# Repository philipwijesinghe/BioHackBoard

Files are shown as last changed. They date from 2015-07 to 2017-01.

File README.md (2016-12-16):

# BioHackBoard

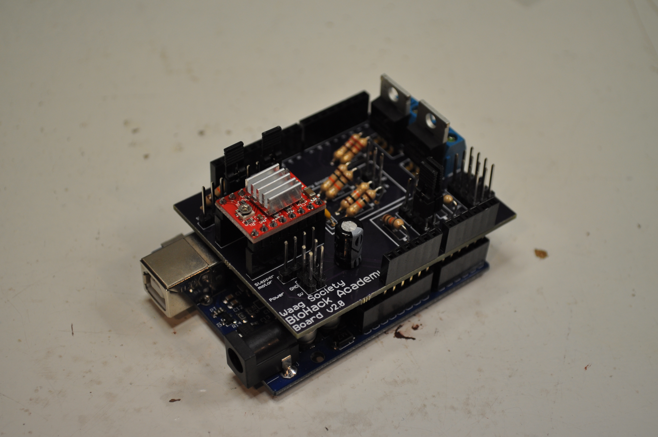
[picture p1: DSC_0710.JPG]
BioHack Board V2.0

The BioHackBaord is an Arduino shield that aims to eliminate the need for any soldering or breadboard for the assembly of BHA devices. 

The shield is able to drive a steppermotor, read a rotary encoders, 2 thermistors, control 2 MOSFETs and connect up to 3 I2C devices, such as an LCD screen.

## Releases

The current version (v2.1) of the board has been designed on the Circuits.io platform. The schematics, PCB design and Gerber files can be found in that [BioHackBoard V2.1 repo](https://circuits.io/circuits/2997842-biohack-board)

The BoM file in this repo lists the parts needed to finish this v2.1 board.

The first version of the board and a kit with additional components was sold by [BioTronics](http://biotronics.nl/products/biohackacademy-prototyping-kit). The source files of this board can be found in this BioHackBoard repository.

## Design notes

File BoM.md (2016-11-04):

## Bill of Materials

These are the parts that need to be soldered on top of a [BioHack Board V2.0](https://circuits.io/circuits/2997842-biohack-board)

### Components 

|No|Amount|Description|Supplier NL|Cost|
| ------------: | ------------: | :------------ | :------------ | ------------: |
|1|2|Screw Terminal|[iPrototype](https://iprototype.nl/products/components/overige/terminal-block-2way), [Farnell](http://nl.farnell.com/multicomp/ma522-500m02/terminal-block-wire-to-brd-2pos/dp/2396252)|0.25|
|2|2|Female header 8 pin|[iPrototype](https://iprototype.nl/products/accessoires/headers/female-headers-8pin-11.5mm)|1.50|
|3|1|Arduino stackable female header set (*1)|[iPrototype](https://iprototype.nl/products/accessoires/headers/female-shield-headers)|1.75|
|4|2|N Channel Power MOSFET|[iPrototype](https://iprototype.nl/products/components/ics/mosfet), [Farnell](http://nl.farnell.com/stmicroelectronics/stp36nf06l/mosfet-n-logic-to-220/dp/9935614)|0.91|
|5|2|10 nF capacitor|[iPrototype](https://iprototype.nl/products/components/capacitors/capacitor-0.01-uf), [Farnell](http://nl.farnell.com/vishay/k103k15x7rf53l2/cap-mlcc-x7r-10nf-50v-rad/dp/1141772)|0.17|
|6|1|100 nF capacitor|[iPrototype](https://iprototype.nl/products/components/capacitors/capacitor-100-uf), [Farnell](http://nl.farnell.com/multicomp/mcgpr10v107m5x11/cap-alu-elec-100uf-10v-rad/dp/1902882)|0.14|
|7|7|10KOhm resistor|[iPrototype](https://iprototype.nl/products/components/resistors/10K), [Farnell](http://nl.farnell.com/te-connectivity/cfr16j10k/resistor-carbon-10k-0-25w-5/dp/2329474)|0.03|
|8|2|220 Ohm resistor|[iPrototype](https://iprototype.nl/products/components/resistors/220R), [Farnell](http://nl.farnell.com/te-connectivity/cfr25j220r/resistor-carbon-220r-0-33w-5/dp/2329643)|0.03|
|9|1|40 Male pin headers|[iPrototype](https://iprototype.nl/products/accessoires/headers/pinheadermale-long), [Farnell](http://nl.farnell.com/wurth-elektronik/61304011121/header-2-54mm-pin-tht-vert-40way/dp/2356175)|0.75|
|10|5|Jumpers|[iPrototype](https://iprototype.nl/products/components/overige/jumper-2pin), [Farnell](http://nl.farnell.com/multicomp/spc20479/shunt-jumper-2pos-code-strip-line/dp/2396301)|0.10|
|11|1|DRV8825 stepper driver|[iPrototype](https://iprototype.nl/products/robotics/drivers-controllers/drv8825-steppermotor-driver)|13.95|

(*1) You can also find these on Farnell, but at a much higher price by combining two [6 pin headers](http://nl.farnell.com/samtec/ssq-106-03-f-s/connector-rcpt-6pos-1row-2-54mm/dp/2578705) with two [8 pin headers](http://nl.farnell.com/samtec/ssq-108-03-f-s/connector-rcpt-8pos-1row-2-54mm/dp/2505051)

**Alternatives**

Look on eBay for much lower prices

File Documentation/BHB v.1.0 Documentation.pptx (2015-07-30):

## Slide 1

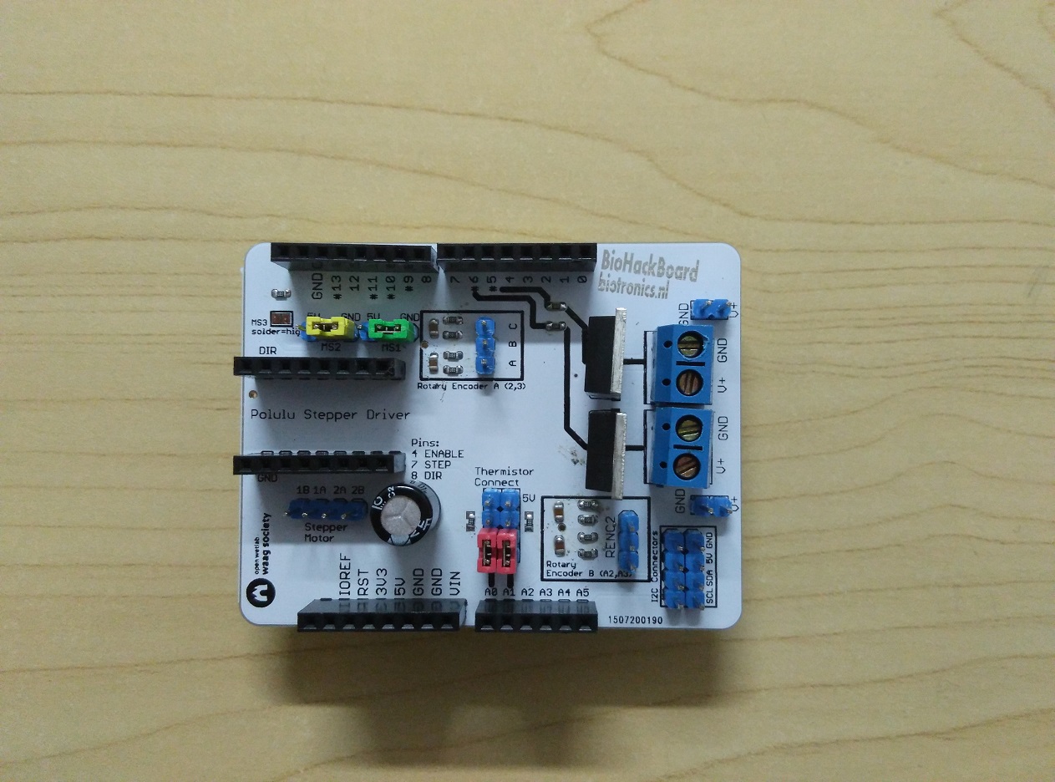
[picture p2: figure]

2 thermistor connections with
voltage divider using a 10k ohm resistor.
Remove the jumpers to use the pins for something else

MS1, MS2 and MS3 control the resolution
of the stepper motor driver

Connect a rotary encoder
(Terminal A, GND, Terminal B)

MOSFET switch (pin 5)
100V 8A

Arduino pins for controlling the stepper driver

MOSFET switch (pin 6)
100V 8A

Two rows of I2C connections.
Usable for I2C LCD panel

Stepper motor connection

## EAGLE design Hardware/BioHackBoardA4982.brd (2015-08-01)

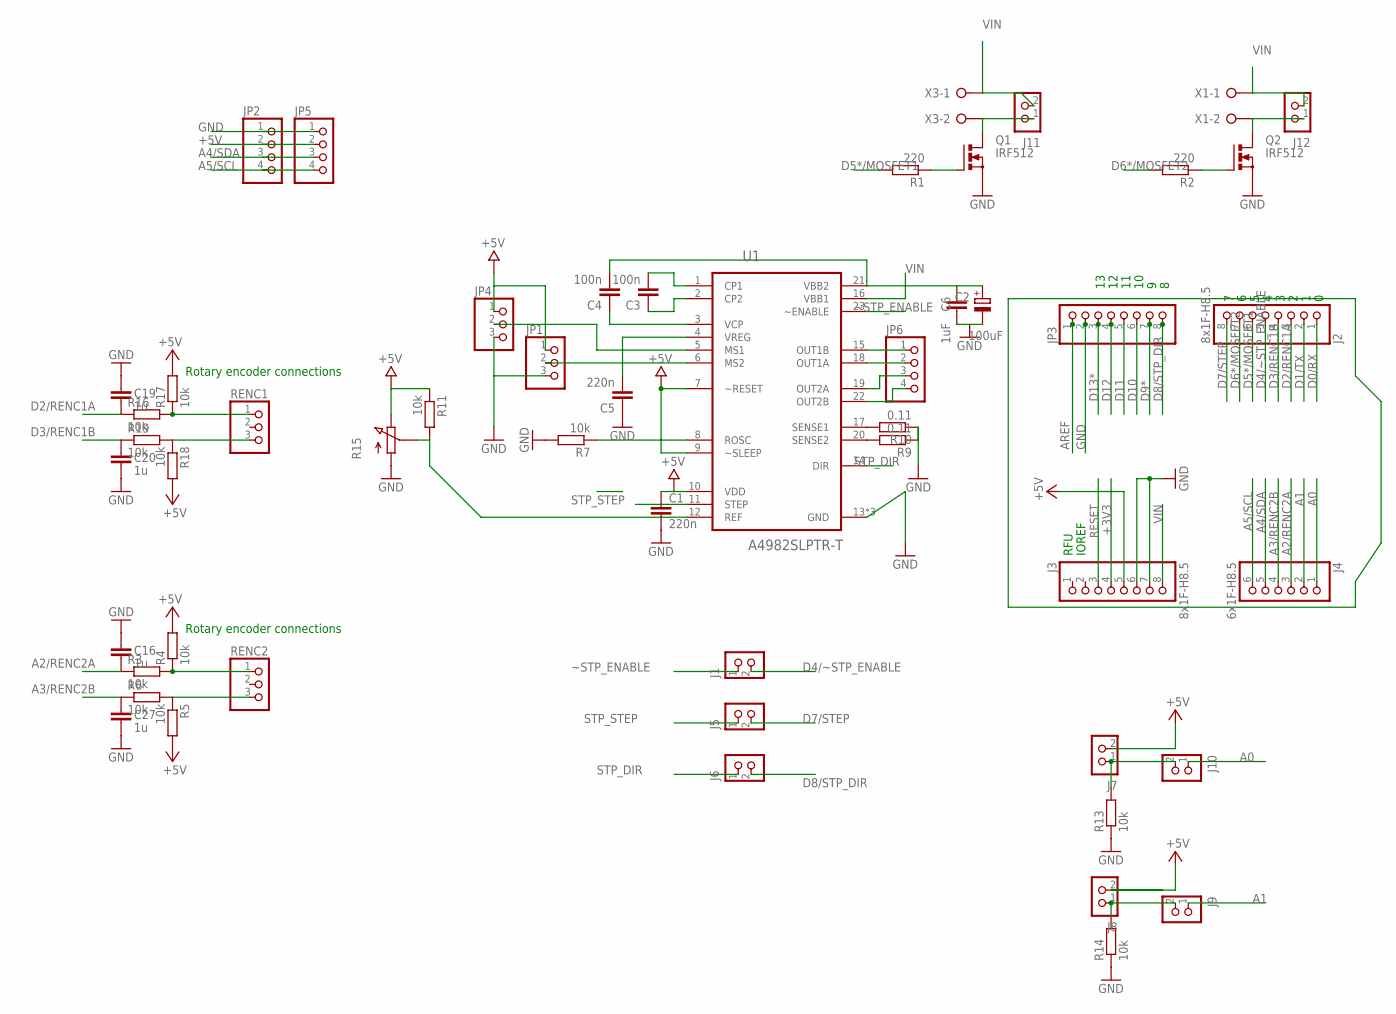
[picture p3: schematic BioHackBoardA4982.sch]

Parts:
C1, C5: 220n; C0805
C2: 100uF; E2,5-5
C3, C4: 100n; C0805
C6: 1uF; C0805
C16, C19, C20, C27: 1u; C0603-ROUND
J1, J5, J6, J7, J8, J9, J10, J11, J12: CON_HEADER_1X02-PTH; M1X2
J2, J3: 8x1F-H8.5; 1X08-S
J4: 6x1F-H8.5; 1X06-S
JP1, JP4: PINHD-1X03_2.54-S; 1X03-S
JP2, JP5, JP6: PINHD-1X04_2.54-S; 1X04-S
JP3: PINHD-1X08_2.54-S; 1X08-S
Q1, Q2: IRF512; TO220BV
R1, R2: 220; R0603-ROUND
R3, R4, R5, R6, R7, R11, R16, R17, R18, R19: 10k; R0603-ROUND
R9, R10: 0.11; R1206
R13, R14: 10k; R0603
R15: PC25
RENC1, RENC2: PINHD-1X03_2.54-S; 1X03-S
U1: A4982SLPTR-T; SOP65P640X120-25N
X1, X3: W237-02P; W237-132

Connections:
+3V3: J3.4
+5V: C1.1, J3.5, J7.2, J8.2, JP1.1, JP2.2, JP4.1, JP5.2, R4.2, R5.2, R11.1, R15.E, R17.2, R18.2, U1.7 (~RESET), U1.9 (~SLEEP), U1.10 (VDD)
A0: J4.1, J10.1
A0P: J7.1, J10.2, R13.2
A1: J4.2, J9.1
A1P: J8.1, J9.2, R14.2
A2/RENC2A: C16.1, J4.3, R3.1
A3/RENC2B: C27.2, J4.4, R6.1
A4/SDA: J4.5, JP2.3, JP5.3
A5/SCL: J4.6, JP2.4, JP5.4
AREF: JP3.1
D0/RX: J2.1
D1/TX: J2.2
D2/RENC1A: C19.1, J2.3, R16.1
D3/RENC1B: C20.2, J2.4, R19.1
D4/~STP_ENABLE: J1.2, J2.5
D5*/MOSFET1: J2.6, R1.2
D6*/MOSFET2: J2.7, R2.2
D7/STEP: J2.8, J5.2
D8/STP_DIR: J6.2, JP3.8
D9*: JP3.7
D10: JP3.6
D11: JP3.5
D12: JP3.4
D13*: JP3.3
GND: C1.2, C2.-, C5.1, C6.1, C16.2, C19.2, C20.1, C27.1, J3.6, J3.7, JP1.3, JP2.1, JP3.2, JP4.3, JP5.1, Q1.S, Q2.S, R7.2, R9.1, R10.1, R13.1, R14.1, R15.A, U1.13 (GND), U1.24 (GND), U1.25 (GND)
MS1: JP4.2, U1.5 (MS1)
MS2: JP1.2, U1.6 (MS2)
unnamed: C4.1, U1.3 (VCP)
unnamed: R7.1, U1.8 (ROSC)
unnamed: C3.2, U1.1 (CP1)
unnamed: C3.1, U1.2 (CP2)
unnamed: R16.2, R17.1, RENC1.1
unnamed: R9.2, U1.20 (SENSE2)
unnamed: R3.2, R4.1, RENC2.1
unnamed: R10.2, U1.17 (SENSE1)
unnamed: Q2.G, R2.1
unnamed: R18.1, R19.2, RENC1.3
unnamed: Q1.G, R1.1
unnamed: R5.1, R6.2, RENC2.3
unnamed: J11.1, Q1.D, X3.2
unnamed: J12.1, Q2.D, X1.2
unnamed: R11.2, R15.S, U1.12 (REF)
OUT1A: JP6.2, U1.18 (OUT1A)
OUT1B: JP6.1, U1.15 (OUT1B)
OUT2A: JP6.3, U1.19 (OUT2A)
OUT2B: JP6.4, U1.22 (OUT2B)
RESET: J3.3
STP_DIR: J6.1, U1.14 (DIR)
STP_STEP: J5.1, U1.11 (STEP)
VIN: C2.+, C4.2, C6.2, J3.8, J11.2, J12.2, U1.16 (VBB1), U1.21 (VBB2), X1.1, X3.1
VREG: C5.2, U1.4 (VREG)
~STP_ENABLE: J1.1, U1.23 (~ENABLE)

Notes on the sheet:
IOREF
RFU
Rotary encoder connections

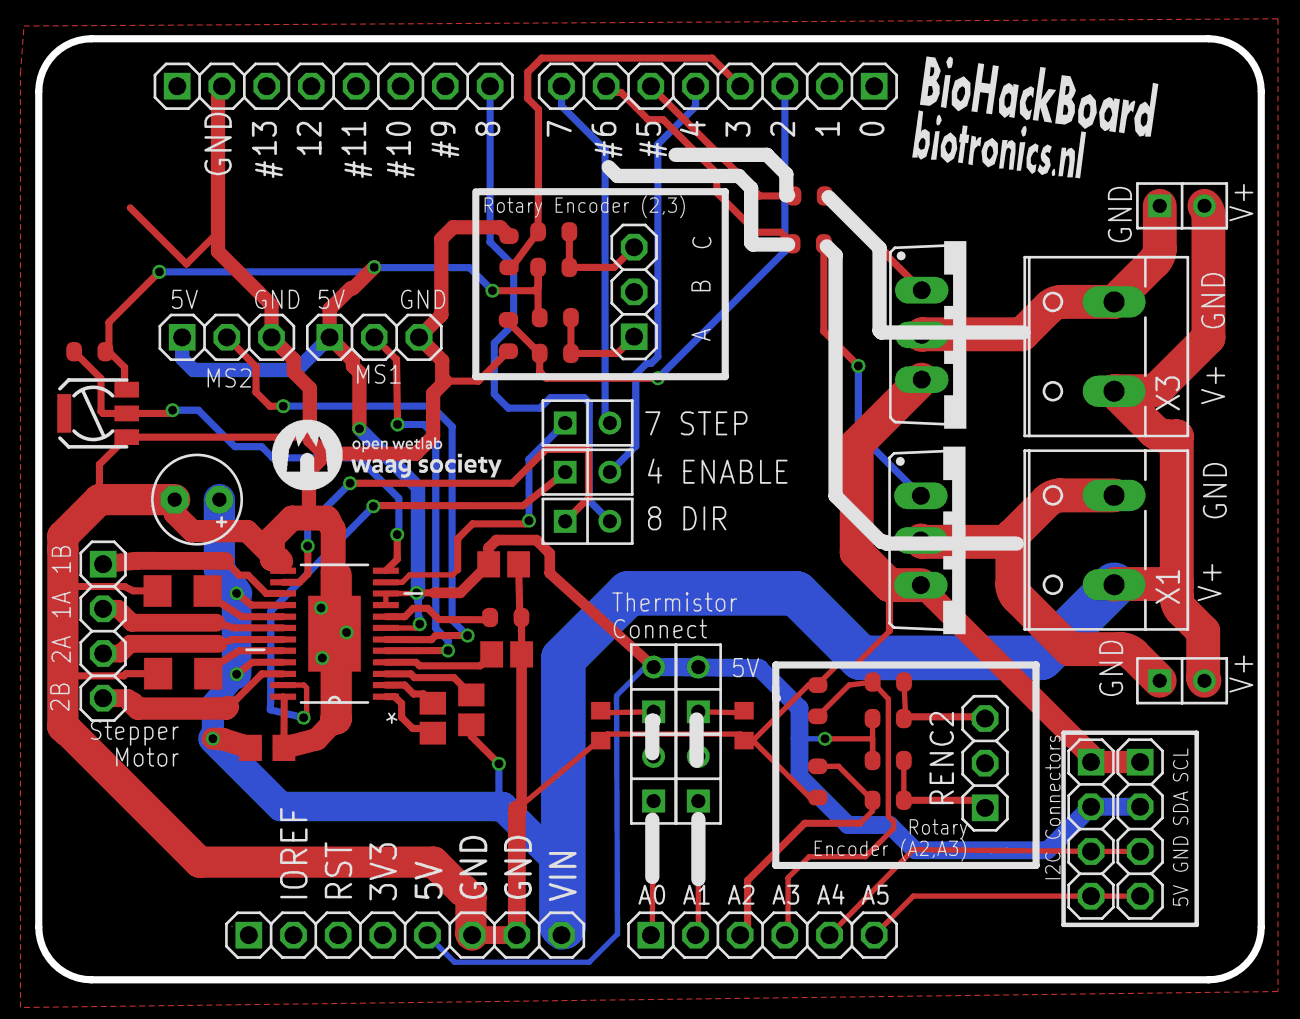
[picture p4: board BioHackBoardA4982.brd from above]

Board: 2 copper layers, 69.5 x 53.5 mm, 52 parts (0 on the bottom side), 43 nets.

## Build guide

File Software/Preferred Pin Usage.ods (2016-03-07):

BioHack Academy Arduino Pin Standards
Pin | BHA Board connections | Preferred Use
0 |  | Hardware Serial
1 |  | Hardware Serial
2 | Rotary encoder 1 interrupt pin
3 | Rotary encoder 1 interrupt pin
4 | Stepper Enable
5 | MOSFET 1
6 | MOSFET 2
7 | Stepper Step
8 | Stepper Direction
9
10
11 |  | Button
12 |  | Button
13 |  | On Board Arduino LED
A0 | Thermistor 1
A1 | Thermistor 2
A2 | Rotary encoder 2 interrupt pin
A3 | Rotary encoder 2 interrupt pin
A4 | I2C SDA
A5 | I2C SCL

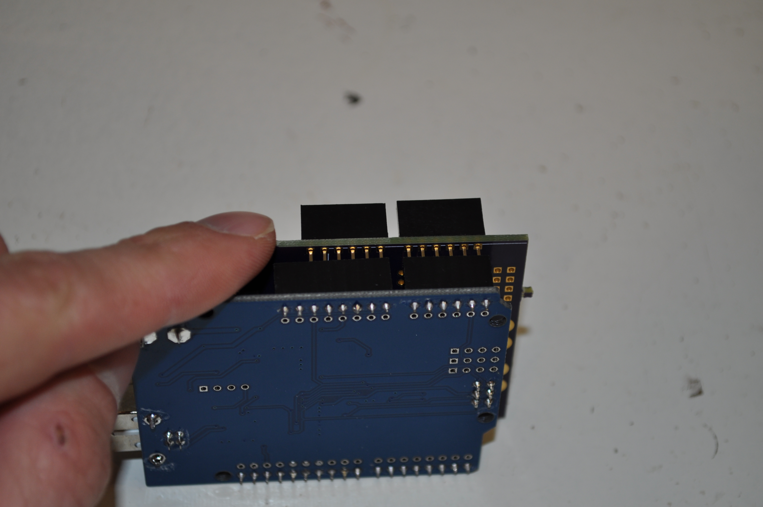
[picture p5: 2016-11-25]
Documentation/BHB v2.0 Assembly Pictures/DSC_0665.JPG

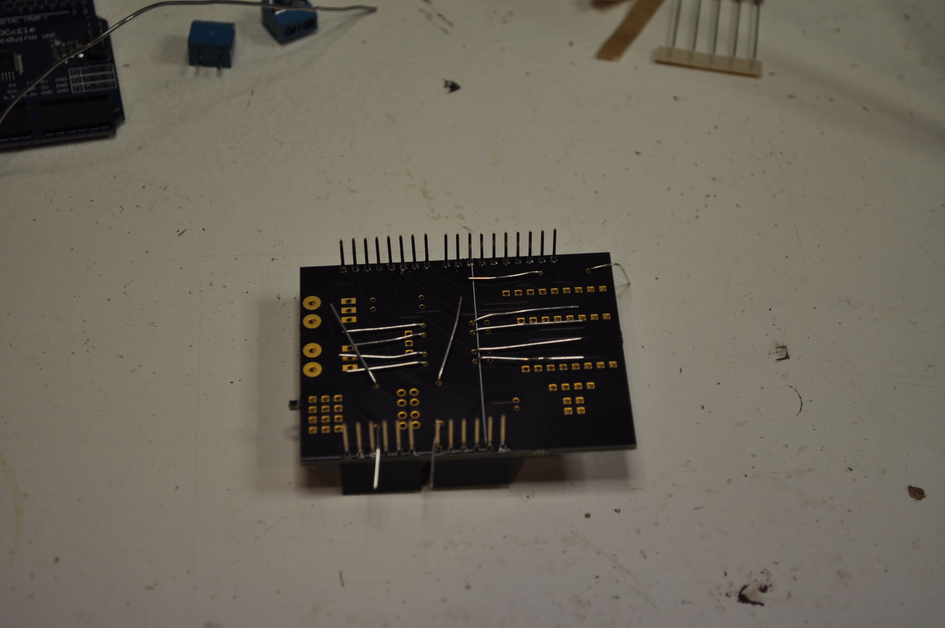
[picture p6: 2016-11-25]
Documentation/BHB v2.0 Assembly Pictures/DSC_0674.JPG

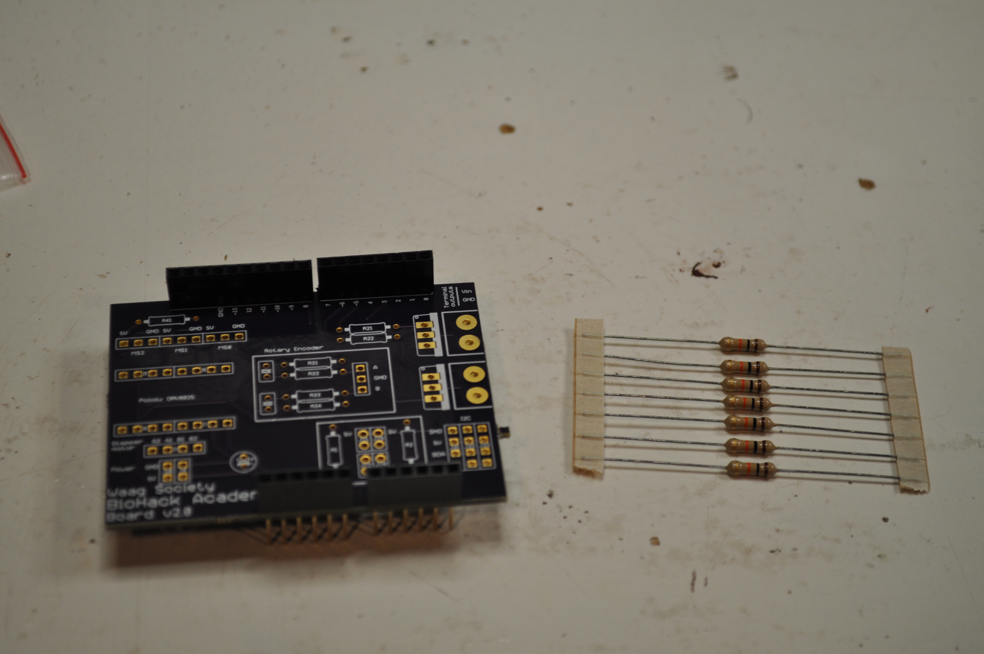
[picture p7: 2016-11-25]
Documentation/BHB v2.0 Assembly Pictures/DSC_0670.JPG

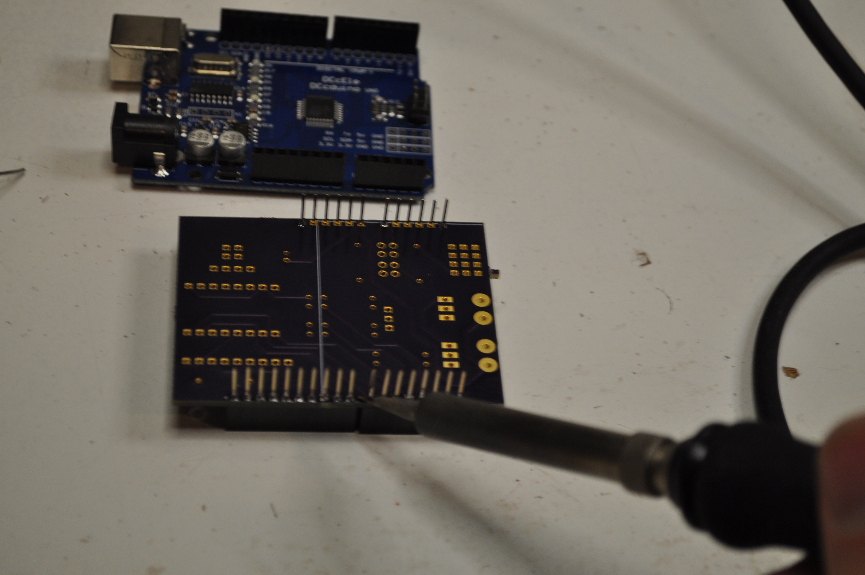
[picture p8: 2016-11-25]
Documentation/BHB v2.0 Assembly Pictures/DSC_0669.JPG

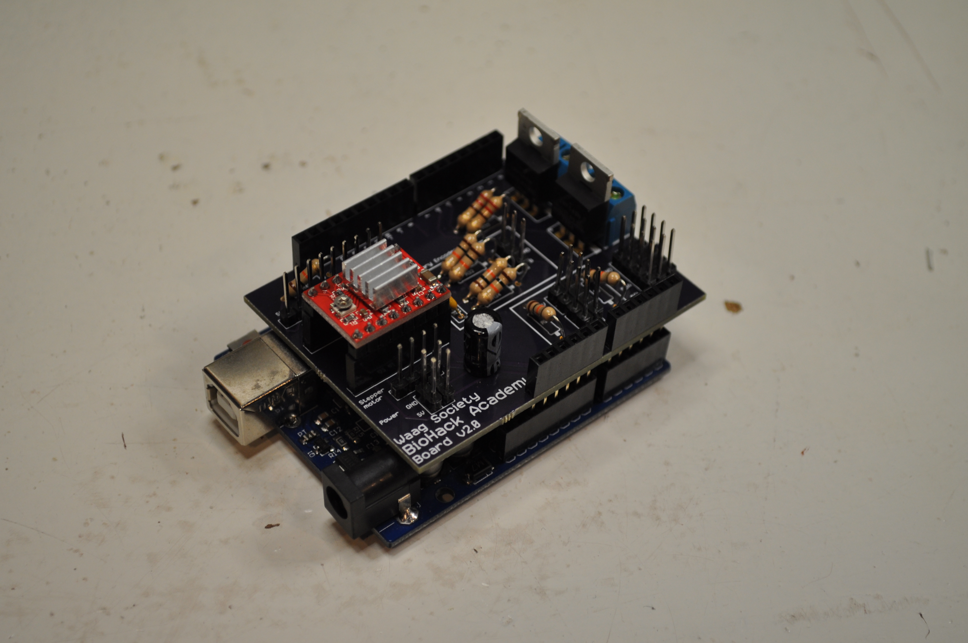
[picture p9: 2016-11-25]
Documentation/BHB v2.0 Assembly Pictures/DSC_0707.JPG

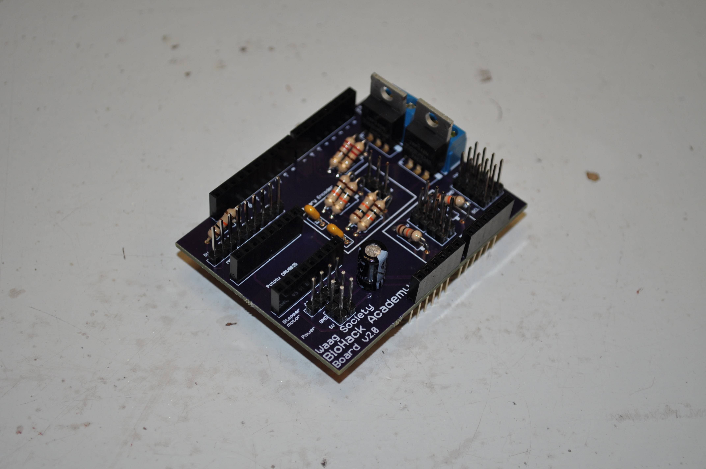
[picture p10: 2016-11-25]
Documentation/BHB v2.0 Assembly Pictures/DSC_0701.JPG

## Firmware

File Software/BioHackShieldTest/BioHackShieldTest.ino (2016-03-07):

#include <Wire.h> // Needed for I2C connection
#include "LiquidCrystal_I2C.h" // Needed for operating the LCD screen
#include <TimerOne.h>
#include <SoftwareSerial.h>

class RotaryEncoder
{
  byte state;
  byte pin0, pin1;
  int value;

  byte readState()
  {
    return (digitalRead(pin0) == HIGH ? 1u : 0u)
         | (digitalRead(pin1) == HIGH ? 2u : 0u);
  }
public:
  RotaryEncoder(int p0, int p1) :
    pin0(p0), pin1(p1), value(0), state(0) {}
  
  void init()
  {
    pinMode(pin0, INPUT);
    pinMode(pin1, INPUT);
    digitalWrite(pin0, 1);  // enable internal pullup
    digitalWrite(pin1, 1);  // enable internal pullup
    value = 0;
    state = readState();
  }

  bool poll()
  {
    // State transition table
    static char tbl[16] =
    { 0, +1, -1, 0,
      // position 3 = 00 to 11, can't really do anythin, so 0
      -1, 0, -2, +1,
      // position 2 = 01 to 10, assume a bounce, should be 01 -> 00 -> 10
      +1, +2, 0, -1,
      // position 1 = 10 to 01, assume a bounce, should be 10 -> 00 -> 01
      0, -1, +1, 0
      // position 0 = 11 to 10, can't really do anything
    };
  
    byte t = readState();
    char movement = tbl[(state << 2) | t];
    if (movement != 0)
    {
      Serial.println((int)t);
      value += movement;
      state = t;
      return true;
    }
    return false;
  }
  
  int getValue()
  {
    return value;
  }
};

RotaryEncoder rotaryEncoderA (2,3);
RotaryEncoder rotaryEncoderB (A2,A3);


// Set the LCD address to 0x27 for a 16 chars and 2 line display
LiquidCrystal_I2C lcd(0x3F,16,2);
float motorSpeed = 0.0f;
byte ledstate = false; // Blinking indicator LED

String buffer;
byte readout;

long last_time;
int stepper_timer=0;
int step_time = 10;
long steps=0;
int  update_timer=0;

byte stepper_en = 0;

const byte PIN_STEP=7; 
const byte PIN_ENABLE=4;
const byte PIN_DIR=8;

const byte PIN_MOSFET0 = 5;
const byte PIN_MOSFET1 = 6;


int mosfet_switch_timer=0;
byte mosfet_index=0;


void scanI2C()
{
  for (int i=0;i<127;i++) {
    Wire.beginTransmission(i);
    byte err = Wire.endTransmission();
    if(err == 0) {
      Serial.print("Device at: " ); Serial.println(i, HEX);
    }
  }
}

void setupLCD() {
  // Initialize I2C
  Wire.begin();
  // Initialize the LCD and print a message
  lcd.init();
  lcd.backlight();
  lcd.clear();
  lcd.setCursor(0,0);
  lcd.print(F("BioHack Academy"));
  lcd.setCursor(0,1);
  lcd.print(F("Peristaltic Pump"));
}

void setup() {
  // Open serial connection and print a message
  Serial.begin(9600);
  Serial.println(F("BioHackShield test"));

  rotaryEncoderA.init();
  rotaryEncoderB.init();
  
  pinMode(PIN_STEP, OUTPUT);
  pinMode(PIN_ENABLE,OUTPUT);
  pinMode(PIN_DIR,OUTPUT);
  
  pinMode(PIN_MOSFET0, OUTPUT);
  pinMode(PIN_MOSFET1, OUTPUT);
  
  stepper_en=1;
  digitalWrite(PIN_ENABLE,1-stepper_en);
  
  setupLCD();
}

void updateLCD()
{
//  lcd.clear();  
  lcd.setCursor(0,0);
  lcd.print(F("Speed: "));
  lcd.print( (int)(motorSpeed) );
  lcd.print(F(" rpm   "));

/*  lcd.setCursor(0,1);
  lcd.print(F("Volume: "));//clear row
  
  const float pi =3.141593f;
  char strbuf[10];
  dtostrf(0.0f, 4, 2, strbuf);
  lcd.print(strbuf);
  lcd.print( " cm3/s");*/
  
  lcd.setCursor(0,1);
  lcd.print("rot: ");
  lcd.print(rotaryEncoderA.getValue());
  lcd.print("   ");
}

void loop() {
  // put your main code here
  long time = millis();
  long dt = time - last_time;
  last_time = time;

  ledstate = 1-ledstate;
  digitalWrite(LED_PIN, ledstate); // alternate between 0 and 1   

  if(stepper_en) {  
    stepper_timer+=dt;
    update_timer+=dt;
  }
    
  if (stepper_timer > step_time && stepper_en) {
    stepper_timer-=step_time;
    digitalWrite(PIN_STEP, 1);
    delay(1);
    digitalWrite(PIN_STEP, 0);
    
    steps++;
  }
  
  mosfet_switch_timer+=dt;
  if (mosfet_switch_timer > 1000) {
    mosfet_switch_timer-=1000;
    
    mosfet_index=1-mosfet_index;
    digitalWrite(PIN_MOSFET0, mosfet_index==0);
    digitalWrite(PIN_MOSFET1, mosfet_index==1);
  updateLCD();
  }
  
  if (update_timer>300 && stepper_en) {
    update_timer-=300;
    Serial.print("steps: ");
    Serial.print(steps);
   
    Serial.print("   A0: ");
    Serial.print(analogRead(A0));

    Serial.print("    A1: ");
    Serial.print(analogRead(A1));
    Serial.println();
  }

  if (rotaryEncoderA.poll()) {
    Serial.print("Encoder A: ");
    Serial.print(rotaryEncoderA.getValue());
    Serial.println();
  }
  
  if (rotaryEncoderB.poll()) {
    Serial.print("Encoder B: ");
    Serial.print(rotaryEncoderB.getValue());
    Serial.println();
  }
      
  while (Serial.available()>0) {
    char c = (char)Serial.read();
    if (c == '\n') {
      if(buffer.startsWith("id")) {
        Serial.println("id:peristaltic-pump"); // so the bioreactor can figure out what is connected 
      }
      else if(buffer.startsWith("i2c")) {
        scanI2C();
      }    
      else if(buffer.startsWith("sp")) {
        int sp = buffer.substring(3).toInt();
        
        Serial.print("setting step time to : ");
        Serial.println(sp);
        
        step_time = sp;
      } else if (buffer.startsWith("en")) {
        stepper_en = 1-stepper_en;
        digitalWrite(PIN_ENABLE,1-stepper_en);
        Serial.println((int)stepper_en);
      } else {
        Serial.println("Unknown cmd.");
      }
      buffer="";
    } else buffer+=c;
  }
}

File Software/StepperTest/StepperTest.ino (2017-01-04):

/*
  This file adds on to the Waag Society's BioHack Academy Code,
  and interfaces with the BioHack Board.

 The code demonstrates how to use the AccelStepper library to drive
 the stepper motor.

 This sketch makes use of the serial port connection to observe the result.
 In case you are unfamiliar with serial port connections check this 
 tutorial: https://www.arduino.cc/en/Tutorial/AnalogReadSerial
 Or have a look at the BHA_SerialCommunication demonstration file
 */

/*
 * INCLUDE LIBRIARIES
 */

/*
Download the AccelStepper library from
http://www.airspayce.com/mikem/arduino/AccelStepper/
There should be a .zip download of the latest version
Install in menus: Sketch/Include Library/Add .ZIP Library
*/
#include <AccelStepper.h>

/*
 * DECLARE VARIABLES AND OBJECTS
 */

// Declare stepper driver pins
const byte PIN_STEP=7;
const byte PIN_DIR=8;
const byte PIN_ENABLE=4;

// Stepper hardware enable toggle
byte stepper_en = 0;

// Declares 'stepper' as an AccelStepper class
// AccelStepper::DRIVER constructs the class to work with a 2 pin 
// contoller: with a step and direction pins.
AccelStepper stepper(AccelStepper::DRIVER,PIN_STEP,PIN_DIR);

// Declare stepper commands
bool runToPos = false;
bool runConst = false;

// These strings hold the serial input and an Int parser, respectively
// For serial interface
String buffer;
String intbuffer;

/*
 * DEFINE LOCAL FUNTIONS
 */

// Handle serial IO
void serial() {
  // Wait for a serial command
  while (Serial.available()>0) {
    char c = (char)Serial.read();
    if (c == '\n') {
      if(buffer.startsWith("id")) {
        Serial.println("id:stepper-test"); // so other devices can figure out what is connected 
      }
      else if(buffer.startsWith("help")) {
        // Help function
        // Display action
        Serial.println("AVAILABLE COMMANDS:");
        Serial.println("id : device id");
        Serial.println("stop : stop stepper");
        Serial.println("moveto <INT> : moves to specified position");
        Serial.println("runspeed <INT> : runs forever at a constant speed");
        Serial.println("accel <INT> : sets acceleration");
        Serial.println("maxspeed <INT> : sets max speed");
        Serial.println("help : displays this menu again");
      } 
      else if(buffer.startsWith("stop")) {
        // Stops stepper
        runToPos = false;
        runConst = false;
        stepper.stop(); //hard stop
        // Clear target position
        int pos = stepper.currentPosition();
        stepper.moveTo(pos);
        // Display action
        Serial.println("Stepper stopped at position:");
        Serial.println((int)pos);
      } 
      else if(buffer.startsWith("runspeed")) {
        // Runs at a constant speed forever
        intbuffer = buffer;
        intbuffer.remove(0,9);
        int spd = intbuffer.toInt();
        stepper.setSpeed(spd);
        runToPos = false;
        runConst = true;
        // Display action
        Serial.println("Running at speed: ");
        Serial.println((int)spd);
      }
      else if(buffer.startsWith("moveto")) {
        // Moves to a relative position
        intbuffer = buffer;
        intbuffer.remove(0,7);
        int dest = intbuffer.toInt();
        stepper.moveTo(dest);
        runToPos = true;
        runConst = false;
        // Display action
        Serial.println("Moving to: ");
        Serial.println((int)dest);
      }
      else if(buffer.startsWith("accel")) {
        // Set acceleration
        intbuffer = buffer;
        intbuffer.remove(0,6);
        int acc = intbuffer.toInt();
        stepper.setAcceleration(acc);
        // Display action
        Serial.println("Accel: ");
        Serial.println((int)acc);
      }
      else if(buffer.startsWith("maxspeed")) {
        // Set max speed
        intbuffer = buffer;
        intbuffer.remove(0,9);
        int mspd = intbuffer.toInt();
        stepper.setMaxSpeed(mspd);
        // Display action
        Serial.println("Max Speed: ");
        Serial.println((int)mspd);
      }
      else if(buffer.startsWith("pos")) {
        int pos = stepper.currentPosition();
        // Display action
        Serial.println("Position: ");
        Serial.println((int)pos);
      }
      else {
        Serial.println("Unknown cmd.");
      }
      buffer="";
    } else buffer+=c;
  }
}

/*
 * SETUP FUNCTION
 */

// Required by Arduino; runs once at reset
void setup() {
  // Open serial connection and print a message
  Serial.begin(9600);
  Serial.println(F("BioHack Board Stepper Test"));
  Serial.println("AVAILABLE COMMANDS:");
  Serial.println("id : device id");
  Serial.println("stop : stop stepper");
  Serial.println("moveto <INT> : moves to specified position");
  Serial.println("runspeed <INT> : runs forever at a constant speed");
  Serial.println("accel <INT> : sets acceleration");
  Serial.println("maxspeed <INT> : sets max speed");
  Serial.println("help : displays this menu again");

  // Setup stepper
  stepper.setMaxSpeed(2000);
  stepper.setAcceleration(100);
}

/*
 * LOOP FUNCTION
 */

void loop() {

  // stepper.run(Speed) should be run as frequently as possible in a loop
  // it will step the stepper if a step is queued at the time.
  if (runToPos) {
    // if a step is queued; steps
    // runs only to desired position
    stepper.run();
  }
  else if (runConst) {
    // runs at a constant speed
    stepper.runSpeed();
  }

  serial();

}

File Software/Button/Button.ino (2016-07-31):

/*
	This file is part of Waag Society's BioHack Academy Code.

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
	You should have received a copy of the GNU General Public License
	along with Waag Society's BioHack Academy Code. If not, see 
	<http://www.gnu.org/licenses/>.

 BHA_Button library demonstration
 
 The code demonstrates how to register a button press only once, instead 
 of multiple times. This is accomplished by measuring the time that has 
 passed since the last registered button press and only registering a new 
 button press after a certain time has passed.

 This sketch makes use of the LED that each Arduino has onboard, 
 connected to pin 13. Other parts the circuit needs are:
 * push button
 * 10K resistor
 Check the "Button Wiring.fzz" file and observe the circuit.

 Derived from
 http://www.arduino.cc/en/Tutorial/Debounce
 */

// Include the BHA button library
#include "BHA_Button.h"

// Constants won't change while the program runs. 
// That's why we use them to set pin numbers
const int buttonPin = 11;    // the number of the pushbutton pin
const int ledPin = 13;      // the number of the LED pin

// Construct BHA_Button class
BHA_Button button(buttonPin);

// Variables will change:
int buttonState;             // the current reading from the input pin

void setup() {
  // declare the pinMode of the ledPin as OUTPUT
  pinMode(ledPin, OUTPUT);

  // set initial LED state
  digitalWrite(ledPin, LOW);
}

void loop() {
  // check button state
  buttonState = button.poll();

  // only switch LED on if the button state is HIGH
  if (buttonState == HIGH) {
    digitalWrite(ledPin, HIGH);
  }
  else {
    digitalWrite(ledPin, LOW);
  }
}

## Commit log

2015-07-30 * BioHackBoard source files
    [BioHackBoardPolulu.brd, BioHackBoardPolulu.sch]
2015-07-30 * Arduino test/example code
2015-08-01 * A4982 stepper driver board. Work in progress (It uses reference design from the datasheet but so far only tested with faulty clone ICs)
    [BioHackBoardA4982.brd, BioHackBoardA4982.sch]
2016-02-10 pin update
    [Preferred Pin Usage.ods]
2016-02-15 BioHackBoard Fritzing file
    [BioHackBoard.fzz]
2016-03-07 * Biohackboard version that's shipped.
    [BioHackBoardPolulu.brd, BioHackBoardPolulu.sch]
2016-07-31 reorganizing files
    [BioHackBoardA4982.brd, BioHackBoardA4982.sch, BioHackBoardPolulu.brd, BioHackBoardPolulu.sch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]
2016-11-25 assembly pictures
2016-12-16 BHA4 update
    [BioHackBoard.fzz]
2017-01-04 Example stepper motor control for BioHack Board
    Added an example for stepper motor control using AccelStepper library.
    It includes acceleration and absolute position tracking.

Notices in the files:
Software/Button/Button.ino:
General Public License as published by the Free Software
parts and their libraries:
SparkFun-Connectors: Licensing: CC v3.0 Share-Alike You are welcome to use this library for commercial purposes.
